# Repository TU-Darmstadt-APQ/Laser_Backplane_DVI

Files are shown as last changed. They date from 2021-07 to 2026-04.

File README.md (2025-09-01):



# Laser Head with fast Modulation Input
This repository contains the [KiCad](https://www.kicad.org/) design files for a compact laser backplane with a DVI connector for application in an ECDL laser system. The laser backplane features a fast current modulation input designed for large-bandwidth laser-frequency stabilization and a laser diode protection circuit. An additional connector for the laser piezo actuator is available.

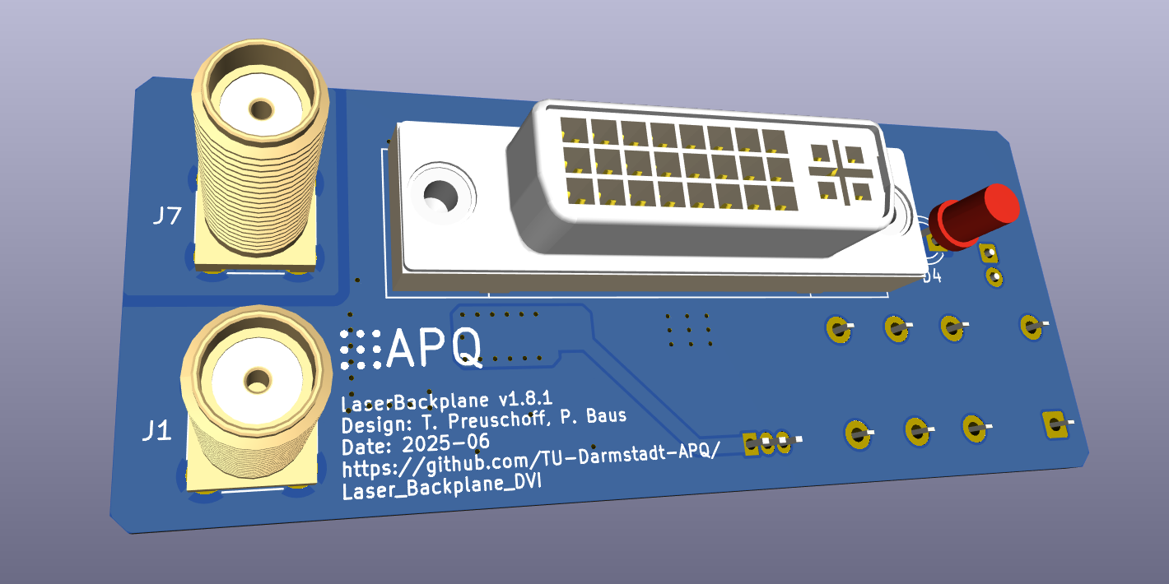
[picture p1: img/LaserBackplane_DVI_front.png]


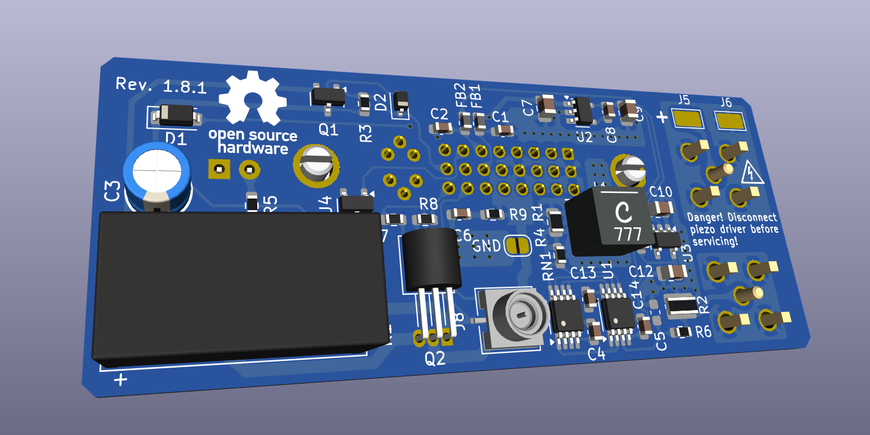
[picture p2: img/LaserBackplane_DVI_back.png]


## Laser diode protection circuit
The protection circuit consists of a relay and a reverse protection diode. The latching relay shorts the laser diode whenever the cable is disconnected or the current driver is turned off. In order to reduce the relay idle current, a latching relay and circuit are used. A fast switching transistor is used as reverse protection diode. The transistor features a very low reverse current leakage and a fast reverse recovery time.

## Fast Current Modulation
The fast modulation input consists of a Howland Current Pump complemented by a passive impedance matching network (see related work for details). It features:
- 3 dB gain flatness DC to 100 MHz
- Phase lag below 90° up to 25 MHz
- Transconductance gain of 1 mA / V
- Input voltage range ±4.8 V

**Note on the compliance voltage**
The compliance voltage of the Howland Current Pump is half of the positive output voltage swing of the operational amplifier. The circuit is implemented by a rail-to-rail output operational amplifier (ADA4807) supplied by ±5 V. Hence, the voltage at the laser diode anode is limited to 2.4 V accounting for a small head-room. Some additional head-room should be reserved for the (small) rise of the voltage required for the maximal output of the current source (5 mA). The maximal laser diode anode voltage is sufficient as a compliance voltage for infra red laser diodes. 

## Pin Configuration

Connector: DVI-I Dual Link (female)

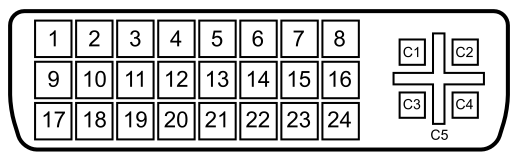
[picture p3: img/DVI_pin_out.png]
Source: https://en.wikipedia.org/wiki/Digital_Visual_Interface#/media/File:DVI_Connector_Pinout.svg


| Pin 		| Signal 		| Description 	|
| --- 		| --- 			|	---			|
|  1 to 5 	|	NC			|				|
|  6  		|	-12 V		|	Negative supply for fast current modulation: -20 V to -5.5 V / 10 mA (max.)	|
|  7		|	EEPROM		|	Optional single wire EEPROM: AT21CS11	|
|  8  		| NC 			|				|
|  9  		| Ld-			| Laser diode cathode current pin 1/2	|
|  10  		| LD+			| Laser diode anode current pin 1/2		|
|  11  		| NC			|				|
|  12  		| Ld-			| Laser diode cathode current pin 2/2	|
|  13  		| LD+			| Laser diode anode current pin 2/2		|
|  14  		|	+12 V		| Positive supply for fast current modulation and protection circuit: 7 V to 18 V / 50 mA (max.) 	|
|  15  		| GND			| Ground reference for power supply	and modulation circuit  |
|  16  		| Relay-		| Connect to GND to switch the relay to 'laser on' state		|
|  17 to 22	| NC			| 				|
|  23  		| V_diode+		| Laser anode voltage sense connection		|
|  24  		| V_diode-		| Laser cathode voltage sense connection	|
|  C1 to C5	| NC			| 				|
|  SH		| NC			| 	Connect the shield to the laser case only			|

## Design Files
The design files can be found on the [releases](../../releases) page and include the following resources:

- Schematics as a PDF
- Gerber files
- Pick & place position files
- Bill of materials as a CSV file and also as an interactive HTML version

The latest revision of those files can be found [here](../../releases/latest).

## Related Work
Review of Scientific Instruments **93**, 063002 (2022); https://doi.org/10.1063/5.0093520

arXiv:2203.06097 [physics.optics]; [https://arxiv.org/abs/2203.06097](https://arxiv.org/abs/2203.06097)

T. Preuschoff, *Laser Technologies for Applications in Quantum Information Science*, Ph.D. thesis, TU Darmstadt, 2023, [https://tuprints.ulb.tu-darmstadt.de/23242/](https://tuprints.ulb.tu-darmstadt.de/23242/)

## License
This work is released under the CERN-OHL-W
See [https://ohwr.org/cern_ohl_w_v2.pdf](https://ohwr.org/cern_ohl_w_v2.pdf) or the included LICENSE file for more information.

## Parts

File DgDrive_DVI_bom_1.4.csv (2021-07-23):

Component | Description | Part | References | Value | Footprint | Quantity Per PCB | Datasheet | MFN | PN | Note | Config
1 | Unpolarized capacitor, small symbol | C_Small | C4 | 1.5p | C_0603_1608Metric | 1 | ~
2 | Unpolarized capacitor, small symbol | C_Small | C1 C2 C8 C11 | 10n | C_0603_1608Metric | 4 | ~ | Kemet Murata Electronics | C0603C103K2RECAUTO GRM1885C1H103JA01J
3 | Unpolarized capacitor, small symbol | C_Small | C7 C9 C10 C12 | 4.7u | C_0805_2012Metric | 4 | ~ | Murata Electronics | GRM21BR61H475KE51L
4 | Polarized capacitor | CP | C3 | 47u | CP_Radial_D5.0mm_P2.00mm | 1 |  | Nichicon | UHV1V470MDD
5 | Diode | D | D1 | BAS21GWX | D_SOD-123 | 1 | ~ | Nexperia | BAS21GWX
6 | Schottky diode | D_Schottky | D2 | BAT54 | D_SOT-23_ANK | 1 |  | STMicroelectronics | BAT54SFILMY | Use a low Vf Schottky
7 | Light emitting diode | LED | D4 | Green | LED_D3.0mm_FlatTop | 1 | ~ | Kingbright | WP424GDT
8 | Ferrite bead, small symbol | Ferrite_Bead_Small | FB1 FB2 | BLM18KG102SZ1D | L_0603_1608Metric | 2 | ~ | Murata | BLM18KG102SZ1D
9 | DVI-I dual link connector | DVI-I | J2 | DVI-I | DVI-I_Conn_Link_CDVI-F29VDG1-P1 | 1 |  | Conn_Link | CDVI-F29VDG1-P1
10 | Omron Low Signal Relay, Single-winding latching type | G6AU | K1 | G6AU | Relay_SPDT_OMRON-G6A | 1 |  | Omron | G6AU-274P-ST-US-DC9
11 | Inductor, small symbol | L_Small | L1 L2 | 3.3u | Coilcraft_XGL3530 | 2 | ~ | Coilcraft | XGL3530-332MEC
12 | NPN transistor, emitter/base/collector | Q_NPN_EBC | Q2 | 2N4401 | TO-92_Inline_Horizontal1 | 1 | ~ | ON Semiconductor | 2N4401BU
13 | 0.2A Ic, 40V Vce, Small Signal NPN Transistor, SOT-23 | MMBT3904 | Q1 | MMBT3904 | SOT-23 | 1 | https://www.fairchildsemi.com/datasheets/2N/2N3904.pdf | Nexperia | MMBT3904VL
14 | Resistor, small symbol | R_Small | R4 | 10 | R_0603_1608Metric | 1 | ~
15 | Resistor | R | R3 R5 R7 R8 | 1k | R_0603_1608Metric | 4 |  | Susumu | RR0816P-102-D
16 | Resistor, small symbol | R_Small | R1 R6 | 49.9 | R_0603_1608Metric | 2 | ~
17 | Resistor, small symbol | R_Small | R2 | 49.9 | R_1210_3225Metric | 1 | ~ | Yageo | RC1210FR-0749R9L
18 | 4 resistor network, parallel topology, split | R_Pack04_Split | RN1 | 10k | MSOP-8_3x3mm_P0.65mm_mod | 1 |  | Vishay | MORNTA1002AT5
19 | Dual Rail-to-Rail Input/Output Amplifiers, MSOP-8 | ADA4807-2ARM | U1 | ADA4807-2ARM | MSOP-8_3x3mm_P0.65mm_mod | 1 | https://www.analog.com/media/en/technical-documentation/data-sheets/ADA4807-1_4807-2_4807-4.pdf | Analog Devices | ADA4807-2ARMZ
20 | MICROPOWER Low Noise 5V 100mA LDO regulator, TSOT-23-5 | LT1761-5 | U2 | LT1761-5 | TSOT-23-5 | 1 | https://www.analog.com/media/en/technical-documentation/data-sheets/1761sff.pdf | Linear Technology | LT1761ES5-5#TRPBF
21 | MICROPOWER 200mA Low Noise LDO negative regulator, fixed output -5V, TSOT-23-5 | LT1964-5 | U3 | LT1964-5 | TSOT-23-5 | 1 | https://www.analog.com/media/en/technical-documentation/data-sheets/1964fb.pdf | Linear Technology | LT1964ES5-5#TRPBF
Component Groups: | 26
Component Count: | 41
Fitted Components: | 33
Number of PCBs: | 1
Total components: | 33
Schematic Version: | 1.4
Schematic Date: | 2021-03-15
PCB Variant: | [u'default']
BoM Date: | 23.07.2021 15:13:04
Schematic Source: | C:\Users\Tilman Preuschoff\Documents\GitHub\Laser_Backplane_DgDrive_DVI\DgDrive_DVI.sch
KiCad Version: | Eeschema (5.1.9)-1

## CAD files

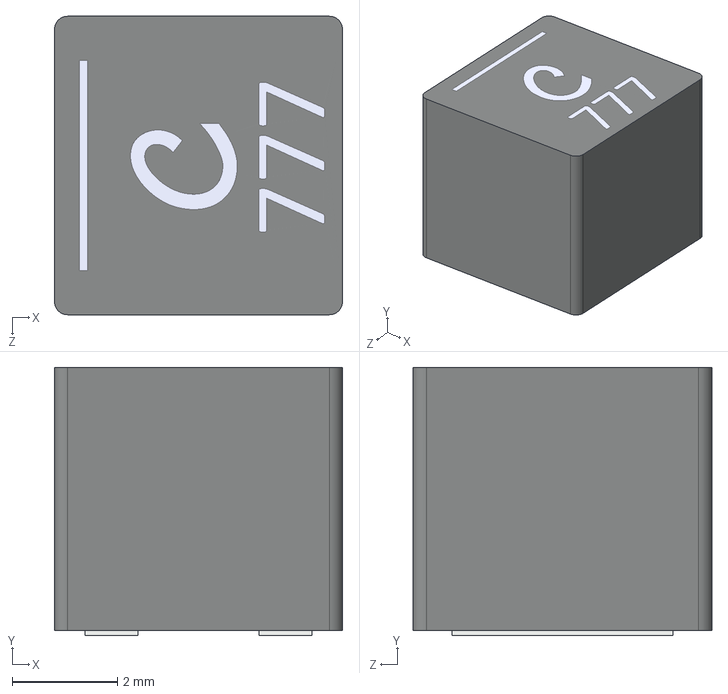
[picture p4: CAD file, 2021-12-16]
KiCad/3D-models/Coilcraft-XAL5050.STEP
5.48 x 5.10 x 5.68 mm

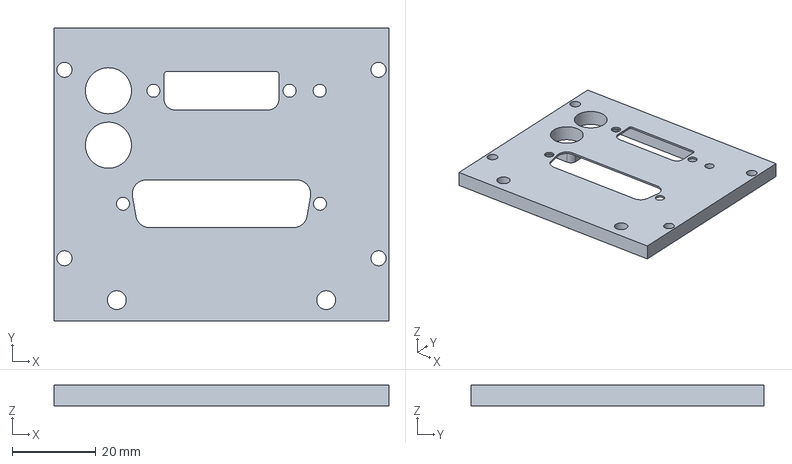
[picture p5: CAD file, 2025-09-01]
mechanical/back_panel.step
80.0 x 70.0 x 5.00 mm

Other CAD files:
mechanical/back_panel.FCStd

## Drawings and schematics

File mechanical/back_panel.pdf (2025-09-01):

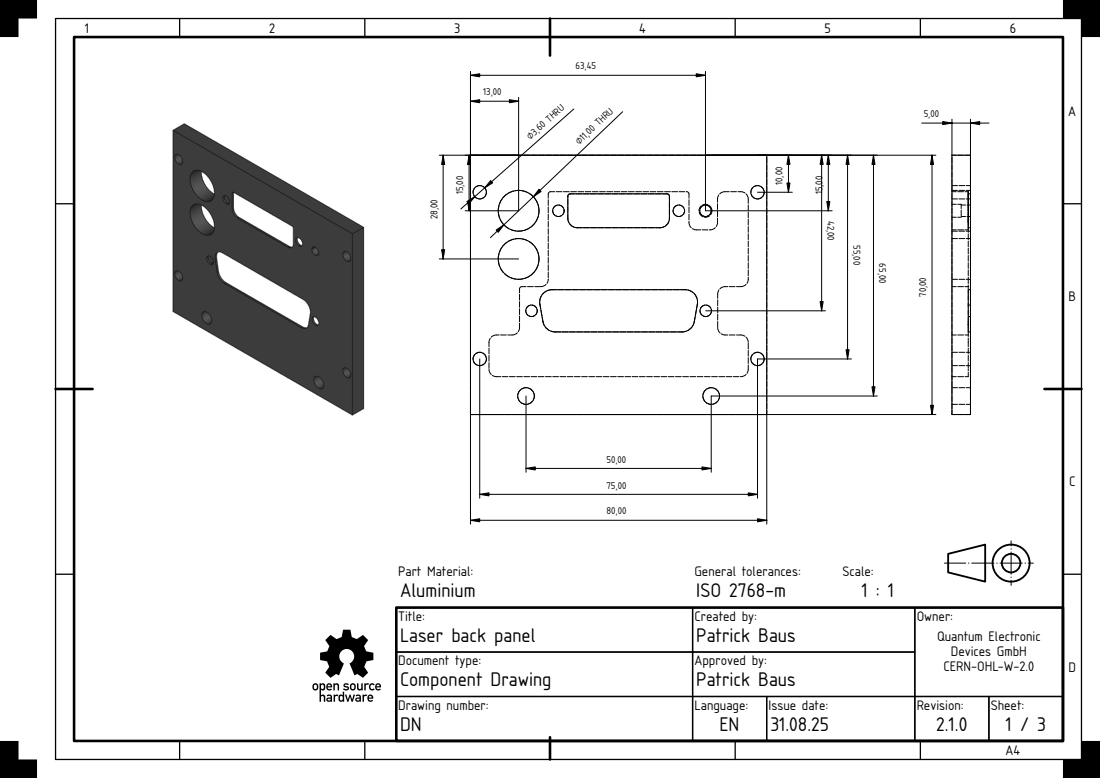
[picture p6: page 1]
Owner:; Drawing number:; Language: Issue date:; Revision:; Sheet:; Approved by:; Created by:; Part Material:; General tolerances:; Scale:; Quantum Electronic Devices GmbH CERN-OHL-W-2.0; Patrick Baus; Aluminium; ISO 2768-m; ⌀3,60 THRU; ⌀11,00 THRU

Title:
Laser back panel
Document type:
Component Drawing

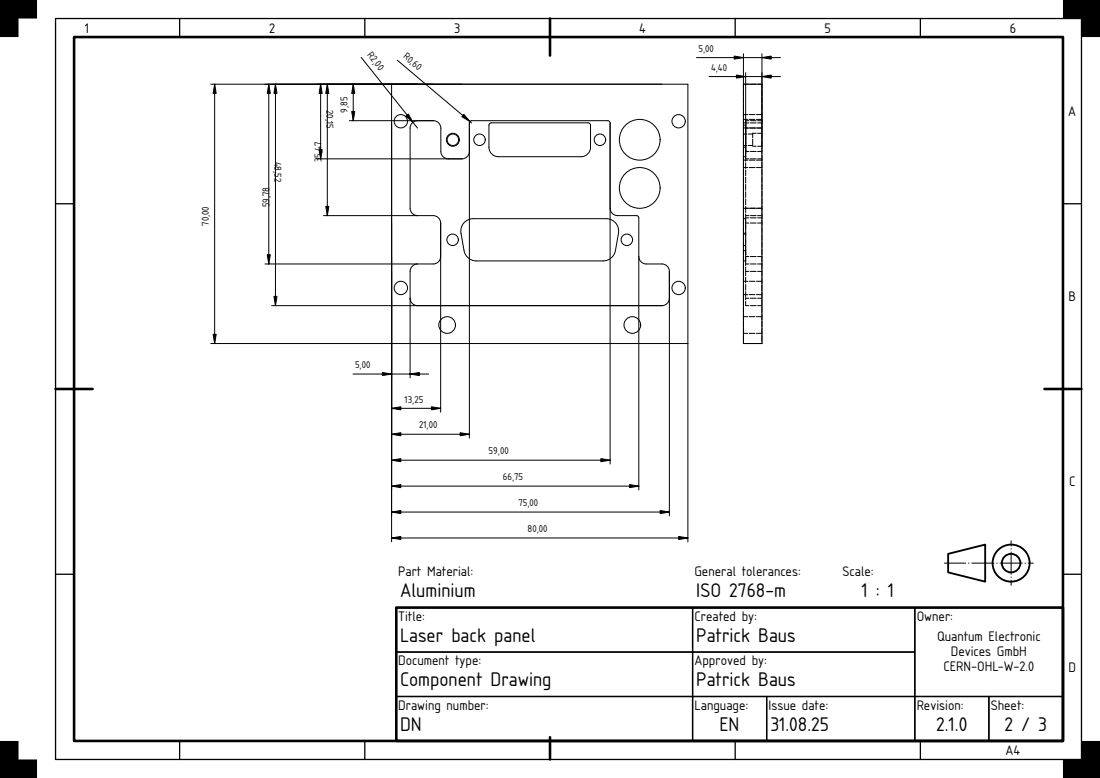
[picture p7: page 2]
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

Title:
Laser back panel
Document type:
Component Drawing

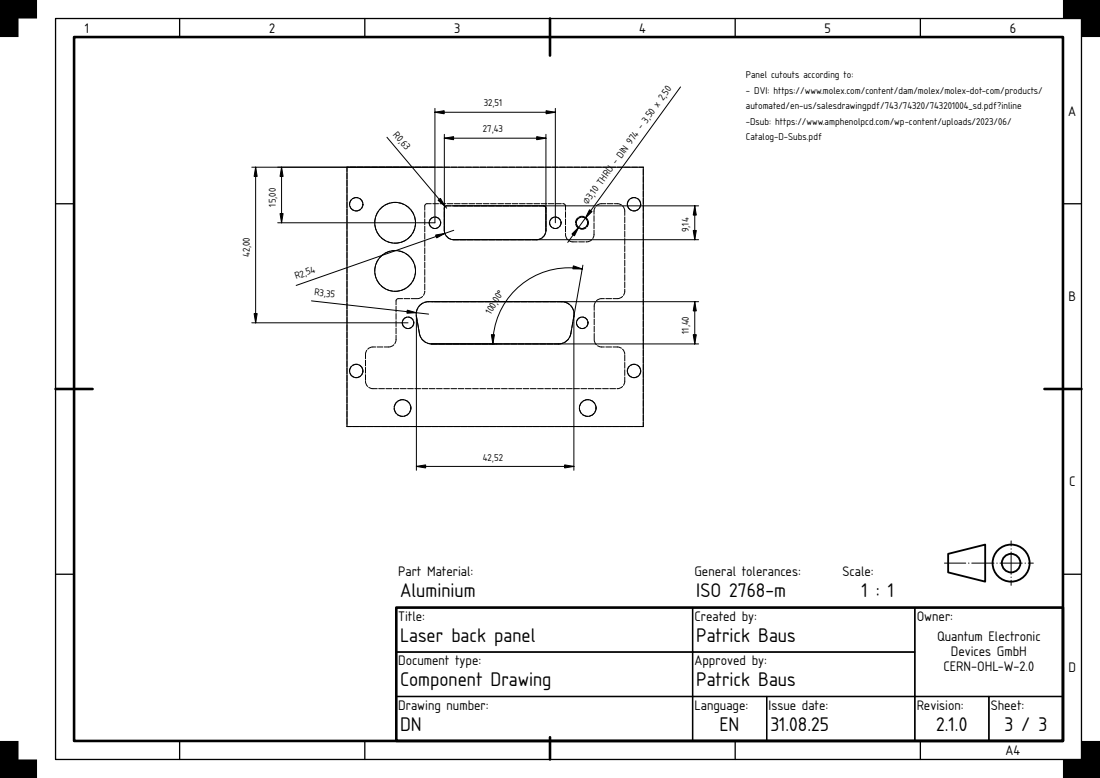
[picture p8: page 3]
Owner:; Drawing number:; Language: Issue date:; Revision:; Sheet:; Approved by:; Created by:; Part Material:; General tolerances:; Scale:; Quantum Electronic Devices GmbH CERN-OHL-W-2.0; Patrick Baus; Aluminium; ISO 2768-m; ⌀3,10 THRU - DIN 974 - 3,50 x 2,50

Panel cutouts according to:
- DVI: https://www.molex.com/content/dam/molex/molex-dot-com/products/
automated/en-us/salesdrawingpdf/743/74320/743201004_sd.pdf?inline
-Dsub: https://www.amphenolpcd.com/wp-content/uploads/2023/06/
Catalog-D-Subs.pdf

Title:
Laser back panel
Document type:
Component Drawing

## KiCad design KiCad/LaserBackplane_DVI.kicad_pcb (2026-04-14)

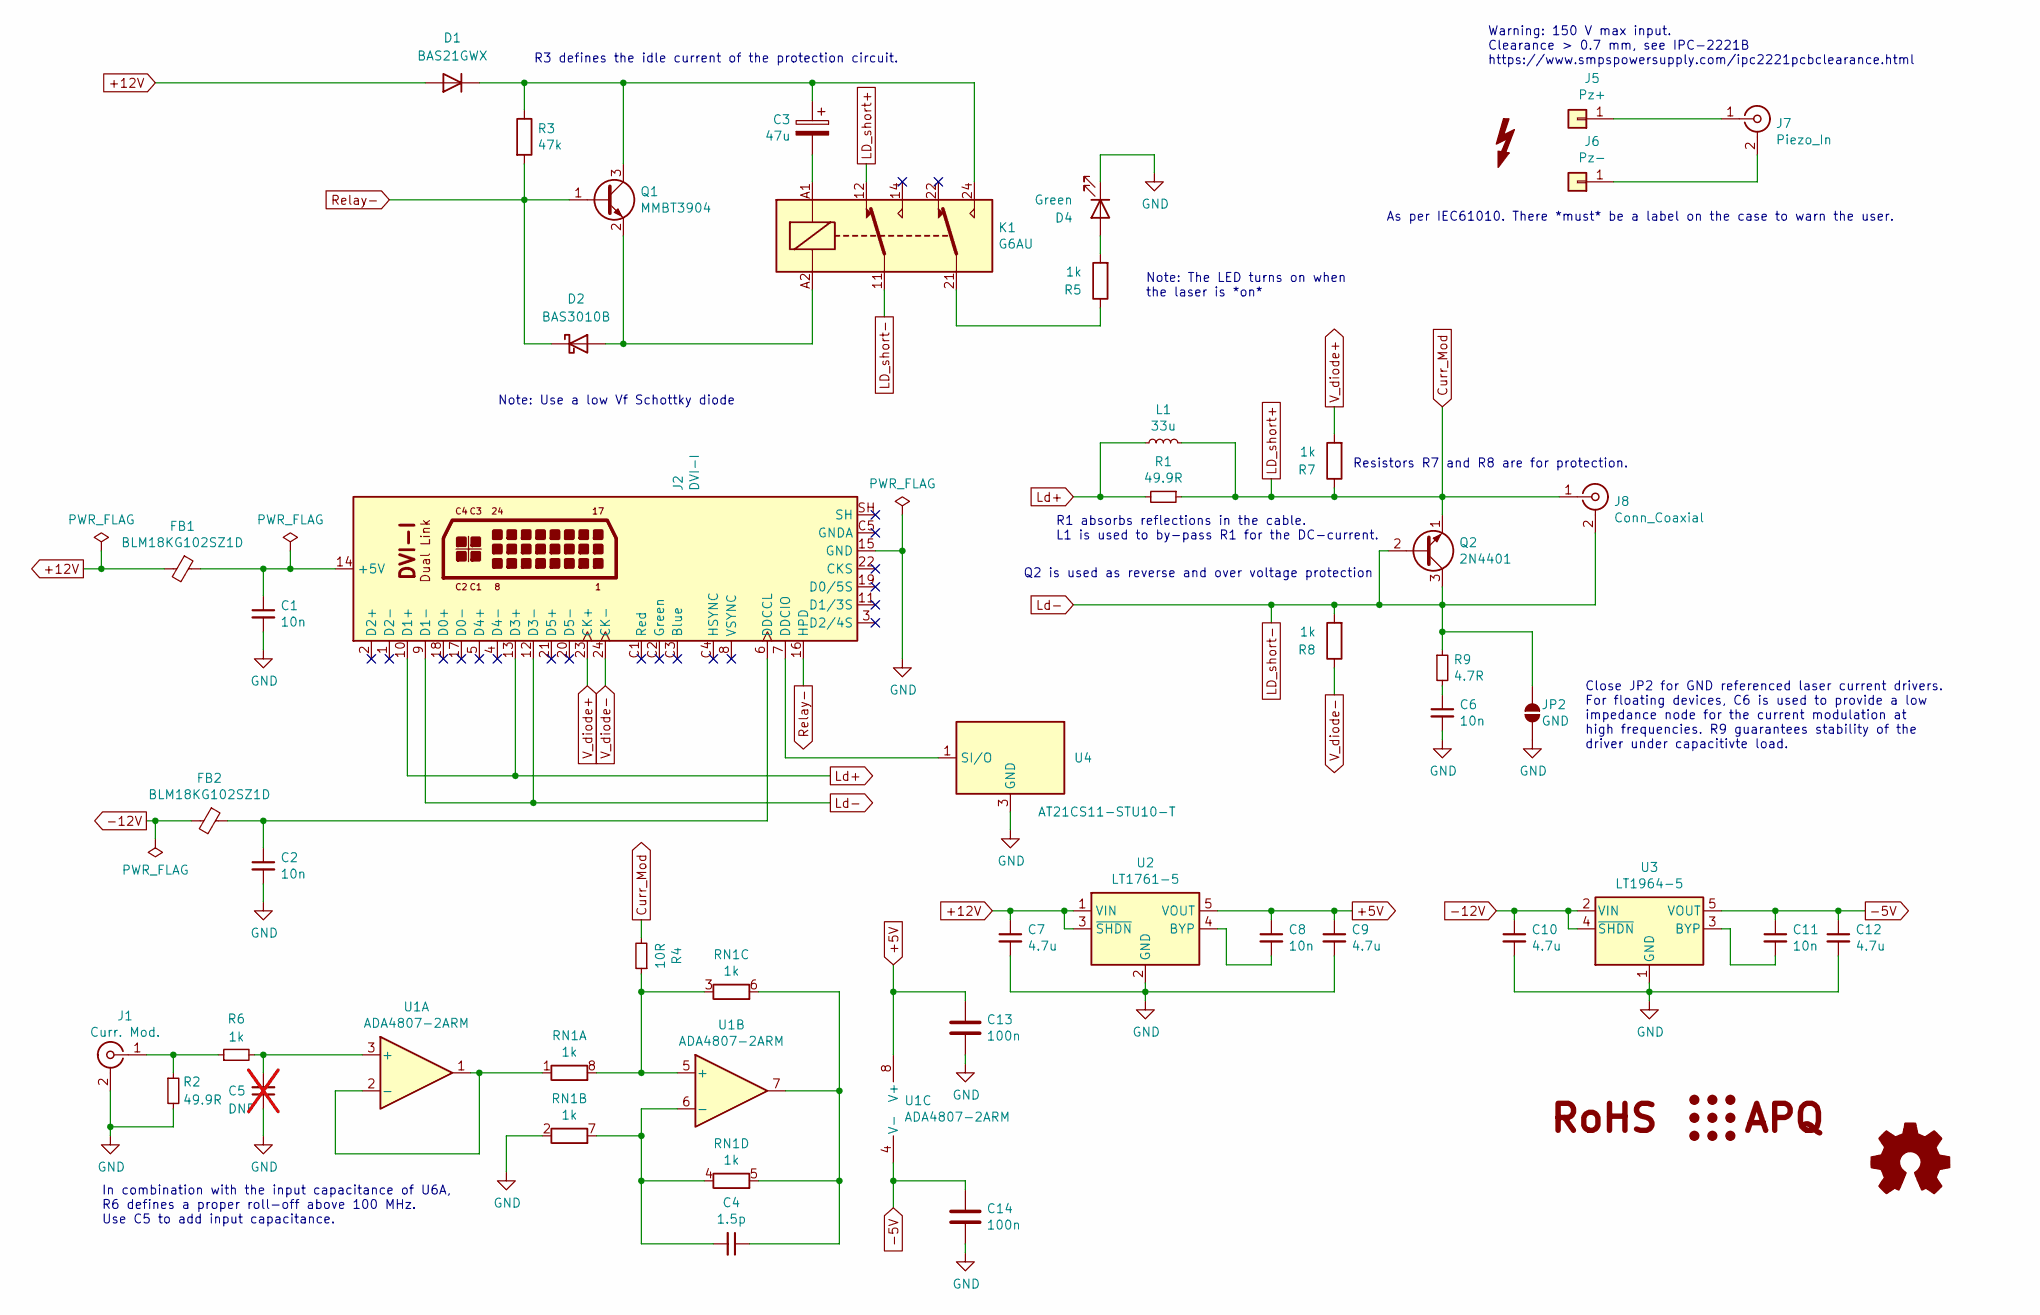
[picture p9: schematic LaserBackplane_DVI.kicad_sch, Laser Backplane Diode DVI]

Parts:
C1, C2, C6, C8, C11: 10n; C_0603_1608Metric
C3: 47u; CP_Radial_D5.0mm_P2.00mm
C4: 1.5p; C_0603_1608Metric
C5: DNF; C_0603_1608Metric; not fitted
C7, C9, C10, C12: 4.7u; C_0805_2012Metric
C13, C14: 100n; C_0603_1608Metric
D1: BAS21GWX; D_SOD-123
D2: BAS3010B; D_SOD-323
D4: Green; LED_D3.0mm_FlatTop
FB1, FB2: BLM18KG102SZ1D; L_0603_1608Metric
J1: Curr. Mod.; SMA_Amphenol_132291_Vertical
J2: DVI-I; DVI-I_Conn-Link_CDVI-F29VDG1-P1_Vertical
J5: Pz+; TestPoint_Keystone_5015_Micro_Mini
J6: Pz-; TestPoint_Keystone_5015_Micro_Mini
J7: Piezo_In; SMA_Amphenol_132291_Vertical
J8: Conn_Coaxial; SMP_TE_CONSMP001-SMD-G-T_Vertical
JP2: GND; SolderJumper-2_P1.3mm_Open_RoundedPad1.0x1.5mm
K1: G6AU; Relay_DPDT_Omron_G6A
L1: 33u; Coilcraft_XGL5050
LOGO1: Logo_APQ; APQ-Logo_small
LOGO2: Logo_Open_Hardware_Small; OSHW-Logo_7.5x8mm_SilkScreen
LOGO3: Logo_RoHS; RoHS-Logo_6mm_SilkScreen
Q1: MMBT3904; SOT-23
Q2: 2N4401; TO-92_Inline_Horizontal1
R1: 49.9R; R_0805_2012Metric
R2: 49.9R; R_0612_1632Metric
R3: 47k; R_0603_1608Metric
R4: 10R; R_0603_1608Metric
R5, R6, R7, R8: 1k; R_0603_1608Metric
R9: 4.7R; R_0603_1608Metric
RN1: 1k; MSOP-8_3x3mm_P0.65mm
SYM1: SYM_Flash_Small; Symbol_HighVoltage_Triangle_3x3mm
U1: ADA4807-2ARM; MSOP-8_3x3mm_P0.65mm
U2: LT1761-5; TSOT-23-5
U3: LT1964-5; TSOT-23-5
U4: AT21CS11-STU10-T; SOT-23

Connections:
+5V: C8.1, C9.1, C13.1, U1.8 (V+), U2.5 (VOUT)
+12V: C7.1, D1.2 (A), FB1.2, U2.1 (VIN), U2.3 (~SHDN)
-5V: C11.1, C12.1, C14.1, U1.4 (V-), U3.5 (VOUT)
-12V: C10.1, FB2.2, U3.2 (VIN), U3.4 (~SHDN)
Curr_Mod: J8.1 (In), K1.12, L1.2, Q2.1 (E), R1.1, R4.2, R7.1
GND: C1.2, C2.2, C5.1, C6.2, C7.2, C9.2, C10.2, C12.2, C13.2, C14.2, D4.1 (K), J1.2 (Ext), J2.15 (GND), JP2.2 (B), R2.2, RN1.2 (R2.1), U2.2 (GND), U3.1 (GND), U4.3 (GND)
LD_short-: J2.9 (D1-), J2.12 (D3-), J8.2 (Ext), JP2.1 (A), K1.11, Q2.2 (B), Q2.3 (C), R8.2, R9.1
Ld+: J2.10 (D1+), J2.13 (D3+), L1.1, R1.2
unnamed: C3.2, K1.A1
unnamed: C6.1, R9.2
unnamed: C3.1, D1.1 (K), K1.24, Q1.3 (C), R3.1
unnamed: D2.2 (A), K1.A2, Q1.2 (E)
unnamed: D4.2 (A), R5.2
unnamed: J1.1 (In), R2.1, R6.1
unnamed: C1.1, FB1.1, J2.14 (+5V)
unnamed: C2.1, FB2.1, J2.6 (DDCCL)
unnamed: J2.7 (DDCIO), U4.1 (SI/O)
unnamed: J5.1, J7.1 (In)
unnamed: J6.1, J7.2 (Ext)
unnamed: K1.21, R5.1
unnamed: RN1.1 (R1.1), U1.1, U1.2 (-)
unnamed: R4.1, RN1.3 (R3.1), RN1.8 (R1.2), U1.5 (+)
unnamed: C4.2, RN1.4 (R4.1), RN1.7 (R2.2), U1.6 (-)
unnamed: C4.1, RN1.5 (R4.2), RN1.6 (R3.2), U1.7
unnamed: C5.2, R6.2, U1.3 (+)
unnamed: C8.2, U2.4 (BYP)
unnamed: C11.2, U3.3 (BYP)
Relay-: D2.1 (K), J2.16 (HPD), Q1.1 (B), R3.2
V_diode+: J2.23 (CK+), R7.2
V_diode-: J2.24 (CK-), R8.1

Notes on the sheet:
R3 defines the idle current of the protection circuit.
Note: The LED turns on when the laser is *on*
Warning: 150 V max input. Clearance > 0.7 mm, see IPC-2221B https://www.smpspowersupply.com/ipc2221pcbclearance.html
Close JP2 for GND referenced laser current drivers. For floating devices, C6 is used to provide a low impedance node for the current modulation at high frequencies. R9 guarantees stability of the driver under capacitivte load.
R1 absorbs reflections in the cable. L1 is used to by-pass R1 for the DC-current.
In combination with the input capacitance of U6A, R6 defines a proper roll-off above 100 MHz. Use C5 to add input capacitance.
Q2 is used as reverse and over voltage protection
Note: Use a low Vf Schottky diode
Resistors R7 and R8 are for protection.
As per IEC61010. There *must* be a label on the case to warn the user.

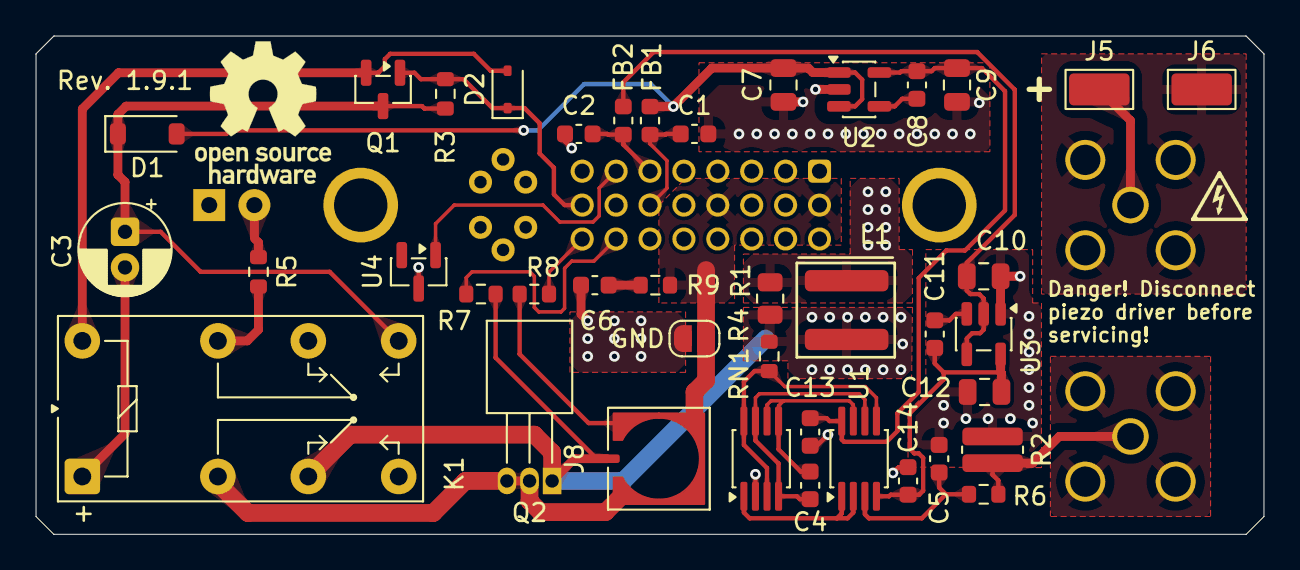
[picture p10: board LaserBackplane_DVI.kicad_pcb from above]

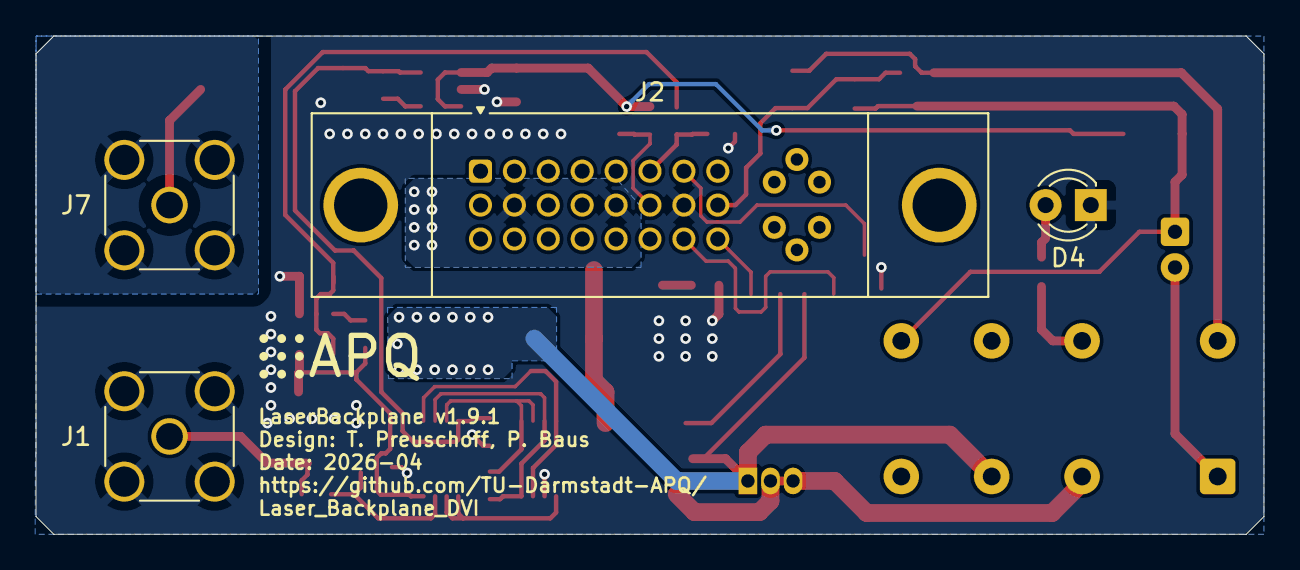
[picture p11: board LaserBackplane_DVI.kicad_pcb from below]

Board: 2 copper layers, 69.0 x 28.0 mm, 47 parts (5 on the bottom side), 30 nets.

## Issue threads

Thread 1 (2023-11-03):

### ISSUE TITLE
Fix DNF components

### ISSUE THREAD

**Issue by PatrickBaus** [TU-Darmstadt-APQ/Laser_Backplane_DVI#1]
There are quite a few components incorrectly marked as DNF. Fix these.

See: https://github.com/TU-Darmstadt-APQ/Laser_Backplane_DVI/releases/download/v1.7.3/schematics_1.7_default.pdf

**Comment by tpreuschoff** [comment]
Added two variants: 'default' without current modulation circuit and 'curr_mod'

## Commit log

2021-03-04 Ld-: SMD Pad for shield
    Fix footprints and replace Ld- THT with SMD pad
    [DgDrive_DVI-B_Cu.gbr, DgDrive_DVI-B_Paste.gbr, DgDrive_DVI-B_SilkS.gbr, DgDrive_DVI-Edge_Cuts.gbr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]
2021-03-15 Incomplete: Add current source
    [DgDrive_DVI.sch]
2021-03-18 Add current source
    Replace Bias-T with Howland current source. The current source requires additional negative supply (Pin7).
    Replace large resistors with inductors+49.9-resistors.
    [DgDrive_DVI-B_Cu.gbr, DgDrive_DVI-B_Fab.gbr, DgDrive_DVI-B_Mask.gbr, DgDrive_DVI-B_Paste.gbr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]
2021-05-12 Updated Gerber files to 1.4 Added EEPROM
    [DgDrive_DVI-B_Cu.gbr, DgDrive_DVI-B_Fab.gbr, DgDrive_DVI-B_Mask.gbr, DgDrive_DVI-B_Paste.gbr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]
2021-07-23 Update BOM
    [DgDrive_DVI.sch, DgDrive_DVI_bom_1.4.csv]
2021-07-23 Fix laser diode polarity
    Switch LD-/LD+ pins at the DVI connector
    [DgDrive_DVI-B_Cu.gbr, DgDrive_DVI-B_Fab.gbr, DgDrive_DVI-B_Mask.gbr, DgDrive_DVI-B_Paste.gbr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]
2021-08-10 Replace XGL3530 with XGL5050
    -Use a larger inductance
    -Options for no inductance at LD- and ground referenced design.
    [DgDrive_DVI-B_Cu.gbr, DgDrive_DVI-B_Fab.gbr, DgDrive_DVI-B_Mask.gbr, DgDrive_DVI-B_Paste.gbr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]
2021-08-20 Update images and pdf schematic
    [DgDrive_DVI_bom_1.5.csv]
2021-10-11 Remove L2
    Remove inductance and bypass resistor at Ld-.
    [DgDrive_DVI-B_Cu.gbr, DgDrive_DVI-B_Fab.gbr, DgDrive_DVI-B_Mask.gbr, DgDrive_DVI-B_Paste.gbr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]
2021-10-13 R3=100k to reduce relay circuit idle current
    This enables activating the laser using a 9V-battery.
    [DgDrive_DVI.sch]
2021-11-02 SMD solder pads for piezo connection
    [DgDrive_DVI-B_Cu.gbr, DgDrive_DVI-B_Fab.gbr, DgDrive_DVI-B_Mask.gbr, DgDrive_DVI-B_Paste.gbr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]
2021-12-16 Current modulation: add input series resitance for proper roll-off and capacitance at Ld- for flat response.
    [DgDrive_DVI.sch]
2021-12-16 Update PCB
    [Coilcraft-XAL5050.STEP, DgDrive_DVI-B_Cu.gbr, DgDrive_DVI-B_Fab.gbr, DgDrive_DVI-B_Mask.gbr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]
2022-01-25 Update to KiCad6
    [DgDrive_DVI.kicad_pcb, DgDrive_DVI.kicad_sch, DgDrive_DVI_bom_1.5.csv, DgDrive_DVI_bom_1.7.csv]
2022-01-25 Update gerber files
    [DgDrive_DVI-B_Cu.gbr, DgDrive_DVI-B_Fab.gbr, DgDrive_DVI-B_Mask.gbr, DgDrive_DVI-B_Paste.gbr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]
2022-01-27 Remove KiCad 5 files and ignore backup files
    [DgDrive_DVI.sch]
2022-01-28 Update DVI connector 3D model
    [74320-3004.0001.ipt, 74320-3004.ipt, 74320-3004.stp, DgDrive_DVI.kicad_pcb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]
2022-02-21 Rename project files
    [LaserBackplane_DVI.kicad_pcb, LaserBackplane_DVI.kicad_sch]
2022-02-21 Add README , BOM, and pdf-schematics
    [74320-3004.0001.ipt, 74320-3004.ipt, 74320-3004.stp, Coilcraft-XAL5050.STEP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]
2022-03-01 Update 3D models
    [74320-3004.0001.ipt, 74320-3004.ipt, 74320-3004.stp, G6AU_274P_ST_US.step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]
2022-05-06 Add alternative part for inductor.
    [LaserBackplane_DVI.kicad_sch]
2022-05-23 Update document information
    [LaserBackplane_DVI.kicad_sch]
2023-10-27 Ignore DNC pads of the DVI connector
2023-10-27 Update DRC filter
2023-11-02 Add variants ('default': without current mod., 'curr_mod': with current mod.)
    [LaserBackplane_DVI.kicad_pcb, LaserBackplane_DVI.kicad_sch, LaserBackplane_DVI_bom_1.7.2_( curr_mod).csv, LaserBackplane_DVI_bom_1.7.2_( default).csv]
2023-11-02 Update revision number
    [LaserBackplane_DVI.kicad_pcb]
2023-11-03 Remove production files
    [DgDrive_DVI-B_Cu.gbr, DgDrive_DVI-B_Fab.gbr, DgDrive_DVI-B_Mask.gbr, DgDrive_DVI-B_Paste.gbr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]
2023-11-03 Remove pdf schematics and COM file
    [LaserBackplane_DVI_bom_1.7.csv]
2023-11-03 Update labels and PCB images
    [LaserBackplane_DVI.kicad_pcb]
2023-11-05 Updated to KiCad 7 Updated footprints
    [LaserBackplane_DVI.kicad_pcb, LaserBackplane_DVI.kicad_sch]
2023-11-05 Fixed variants
    [LaserBackplane_DVI.kicad_pcb, LaserBackplane_DVI.kicad_sch]
2023-11-05 Added 3d model to XAL5050 inductor
    [LaserBackplane_DVI.kicad_pcb]
2023-11-15 Replace DNF by 'exclude from bom' for solder pads and logos.
    [LaserBackplane_DVI.kicad_pcb, LaserBackplane_DVI.kicad_sch]
2023-11-20 Add back panel
    [back_panel.0005.dwg, back_panel.0024.ipt, back_panel.dwg, back_panel.ipt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]
2023-11-20 Update PCB images
2024-05-14 Update to KiCad 8 (#4)
    * Update to KiCad 8
    Removed obsolete libs and footprints
    * Updated symbols
    * Replaced EOL parts
    * Swapped 50 ohm resistor for a higher wattage part
    * Added bypass capacitors to the current source opamp
    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
    [LaserBackplane_DVI.kicad_pcb, LaserBackplane_DVI.kicad_sch]
2024-05-14 Update README.md
    Add whitespace to push DVI connector pinout to the next line
2024-10-18 1.7.4 (#5)
    * Add chamfer to corners
    * Change line with of the part dimentsions to 0.1 mm
    * Add teardrops
    * Added peizo driver high voltage warning
    * Add PCBA variant
    * Cleaned up labels
    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
    [LaserBackplane_DVI.kicad_pcb, LaserBackplane_DVI.kicad_sch]
2025-02-17 Replaced X7R 10nF Capacitors with C0G (#6)
    * Replaced 10nF X7R CGA3E2X7R1H103K080AA with C0G CGA3E2C0G1H103J080AE
    * Added letter "R" to resistor values that do not have an SI suffix
    * Updated LED footprint for KiCAD 8.0.8
    * Added missing high voltage footprint
    [LaserBackplane_DVI.kicad_pcb, LaserBackplane_DVI.kicad_sch]
2025-06-24 Update/kicad9 (#7)
    * Bump to KiCad 9
    * Bump version to 1.8.0
    [LaserBackplane_DVI.kicad_pcb, LaserBackplane_DVI.kicad_sch]
2025-06-24 Updated DVI connector footprint (#8)
    [LaserBackplane_DVI.kicad_pcb, LaserBackplane_DVI.kicad_sch]
2025-06-26 Changed laser diode connector form solder connection to SMP (#9)
    [LaserBackplane_DVI.kicad_pcb, LaserBackplane_DVI.kicad_sch]
2025-06-26 Removed paste layer from piezo solder pads (#10)
    [LaserBackplane_DVI.kicad_pcb]
2025-06-26 Fixed SMP connector symbol. Removed incorrect 3D model (#11)
    * Fixed SMP connector symbol. Removed incorrect 3D model
    [LaserBackplane_DVI.kicad_pcb]
2025-06-26 Drop relay 3d model no longer needed (#13)
    [G6AU_274P_ST_US.stp]
2025-06-26 Replaced incorrect 3D model of the DVI connector (#12)
    * Removed incorrect 3D model of the DVI connector
    * Added 3D correct model of the DVI connector
    * Replaced SMA connector footprint with correct one
    [LaserBackplane_DVI.kicad_pcb, LaserBackplane_DVI.kicad_sch]
2025-06-26 Do not place the LED for assembly as this needs to match the frontpanel mounting hole (#15)
    [LaserBackplane_DVI.kicad_pcb, LaserBackplane_DVI.kicad_sch]
2025-06-26 Change R3 from 100k to 47k to increase the current through the relay during switch off (#16)
    [LaserBackplane_DVI.kicad_pcb, LaserBackplane_DVI.kicad_sch]
2025-06-26 Bump to 1.8.1 (#17)
    Updated authors
    [LaserBackplane_DVI.kicad_pcb, LaserBackplane_DVI.kicad_sch]
2025-06-27 Added current mod PCBA files (#18)
    * Added current mod + PCBA files
    * Correctly skip ERC/DRC when requested
    * Add more ERC/DRC warning filters
    * Do not place the current mod SMA when using the PCBA service.
    [LaserBackplane_DVI.kicad_pcb, LaserBackplane_DVI.kicad_sch]
2025-06-27 Fix/version (#19)
    * Fixed incorrect version label
    * Refilled zones
    * Updated images
    [LaserBackplane_DVI.kicad_pcb]
2025-06-28 Fixed product number of the relay (#22)
    - Removed the dash before DC9 at the end of the relay PN.
    [LaserBackplane_DVI.kicad_pcb, LaserBackplane_DVI.kicad_sch]
2025-08-31 Fixed alignment issues (#25)
    * Fixed alignment issues
    - Moved the LED D4 up by 0.5 mm to match the DVI connector y position
    - Moved the DVI connector 0.005 mm to the right to center it on the PCB
    - Updated DVI footprint to center it on pin 14
    - Redrawn draces connecting the DVI connector
    - Moved piezo labels slighty down and away from the edge
    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
    [LaserBackplane_DVI.kicad_pcb, LaserBackplane_DVI.kicad_sch]
2025-08-31 Updated EEPROM symbol (#26)
    Updated the EEPROM symbol and enabled more ERC rules. Renamed the symbol from AT21CS11-STXXXX-X to AT21CS11-STU10‑T.
    [LaserBackplane_DVI.kicad_pcb, LaserBackplane_DVI.kicad_sch]
2025-09-01 Fixed design issues with the back panel (#27)
    - Replaced Inventor with FreeCad
    - Added pocket for the through-hole capacitor C3
    - Fixed connector dimensions
    - Changed depth of the pocket to the same depth for all pockets
    - The second SMA connector is now drilled out by default
    [back_panel.0005.dwg, back_panel.0024.ipt, back_panel.FCStd, back_panel.dwg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]
2026-04-14 Bump to KiCad 9.0.7 (#36)
    Updated PCB to 1.9.1
    [LaserBackplane_DVI.kicad_pcb, LaserBackplane_DVI.kicad_sch]
2026-04-14 Bump PCB version
    [LaserBackplane_DVI.kicad_pcb]

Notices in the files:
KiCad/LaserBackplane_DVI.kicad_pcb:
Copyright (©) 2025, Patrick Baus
